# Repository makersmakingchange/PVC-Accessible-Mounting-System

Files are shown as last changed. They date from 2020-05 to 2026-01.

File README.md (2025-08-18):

# PVC Assistive Mounting System

The PVC Assistive Mounting System is a collection of readily available commercial-off-the-shelf components and 3D printed components that can be assembled into various configurations to provide mounting solutions for assistive technology.

## Configurations

### LipSync Desk Mount
The [LipSync Desk Mount](/Configurations/LipSync_Desk_Mount/README.md) provides a low cost, adjustable system to mount the [LipSync Classic](https://github.com/makersmakingchange/LipSync-Classic) to a flat surface like a table or desk.

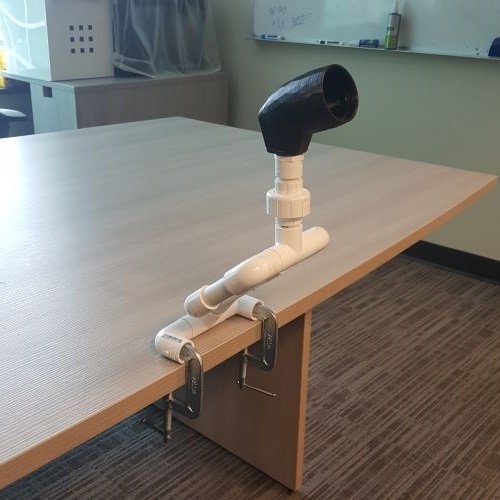
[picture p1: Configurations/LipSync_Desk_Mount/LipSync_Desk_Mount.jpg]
LipSync Desk Mount


### Small Button Mount
The [Small Button Mount](/Configurations/Small_Button_Mount/README.md) is a simple, inexpensive mounting solution to position a small button on a flat surface.

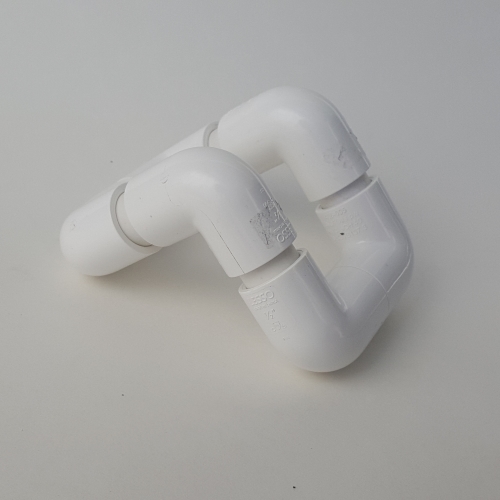
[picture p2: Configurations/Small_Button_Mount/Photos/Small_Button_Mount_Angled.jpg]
Small Button Mount


### Large Button Mount
Work-in-progress

## Components
### Camera Quick Clamp
The [PAMS Camera Quick Clamp](Components/PAMS_Camera_Quick_Clamp/README.md) is a 3D printed adapter for attaching an assistive device to a section of 1/2 inch PVC piping. The clamp has a ¼”- 20 UNC camera thread stud that is compatible with various assistive devices and/or camera mount adapters. The clamp can easily be installed, adjusted, and removed by hand.

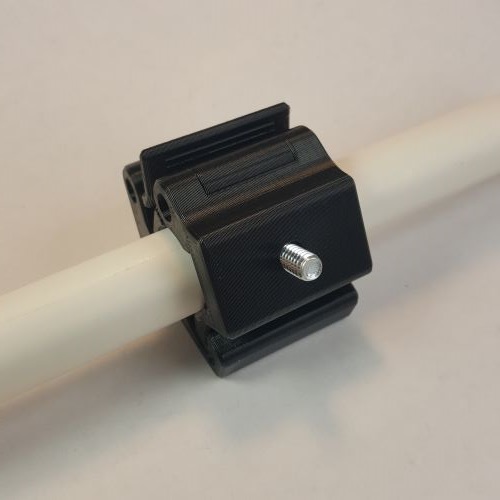
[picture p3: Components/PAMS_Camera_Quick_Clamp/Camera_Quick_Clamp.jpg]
PAMS Camera Quick Clamp


### Super Clamp Adapter
Work-in-progress

### Round Tubing Clamp
Work-in-progress

### Wheelchair Rail adapter
Work-in-progress

## Resources
More information for working with PVC: [PVC Resources](/Resources/README.md)

## License
<br /><span xmlns:dct="http://purl.org/dc/terms/" property="dct:title">PVC Accessible Mounting System</span> by <a xmlns:cc="http://creativecommons.org/ns#" href="www.makersmakingchange.com" property="cc:attributionName" rel="cc:attributionURL">Neil Squire</a> is licensed under a <a rel="license" href="http://creativecommons.org/licenses/by-sa/4.0/">Creative Commons Attribution-ShareAlike 4.0 International License</a>.

<!-- ABOUT MMC START -->
## About Makers Making Change
[Makers Making Change Logo](https://www.makersmakingchange.com/)

Makers Making Change is a program of [Neil Squire](https://www.neilsquire.ca/), a Canadian non-profit that uses technology, knowledge, and passion to empower people with disabilities.

Makers Making Change leverages the capacity of community based Makers, Disability Professionals and Volunteers to develop and deliver affordable Open Source Assistive Technologies.

 - Website: [www.MakersMakingChange.com](https://www.makersmakingchange.com/)
 - GitHub: [makersmakingchange](https://github.com/makersmakingchange)
 - Bluesky: [@makersmakingchange.bsky.social](https://bsky.app/profile/makersmakingchange.bsky.social)
 - Instagram: [@makersmakingchange](https://www.instagram.com/makersmakingchange)
 - Facebook: [makersmakechange](https://www.facebook.com/makersmakechange)
 - LinkedIn: [Neil Squire Society](https://www.linkedin.com/company/neil-squire-society/)
 - Thingiverse: [makersmakingchange](https://www.thingiverse.com/makersmakingchange/about)
 - Printables: [MakersMakingChange](https://www.printables.com/@MakersMakingChange)

### Contact Us
For technical questions, to get involved, or to share your experience we encourage you to [visit our website](https://www.makersmakingchange.com/) or [contact us](https://www.makersmakingchange.com/s/contact).
<!-- ABOUT MMC END -->

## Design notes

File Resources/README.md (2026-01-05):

# PVC Resources

## Suppliers
PVC is readily available at hardware stores.

Home Depot [Canada](https://www.homedepot.ca/)
 - PVC Pipe
 - Standard fittings
 - Tools

Amazon
[Ventral](https://www.amazon.ca/PVC-Pipe-SCH-Inch-White/dp/B00V67XP0)

[McMaster-Carr](https://www.mcmaster.com/)
 - Pipe [5ft](https://www.mcmaster.com/48925K91) [10ft](https://www.mcmaster.com/48925K11)
 - [Fittings](https://www.mcmaster.com/pvc-(schedule-40)-pipe-fittings)

[PVCFittingsOnline](https://www.pvcfittingsonline.com/)
 - Pipe
 - Standard fittings
 - Specialized Fittings
 - Tools

[FORMUFIT](https://formufit.com/)
 - Furniture Grade PVC and SCH 40 PVC in various sizes and colors
 - Specialized Fittings
 - Colored PVC Shrink Covering
 - How-to Guides

 [Lee Valley](https://www.leevalley.com/)
  - [Specialized fittings](https://www.leevalley.com/en-us/shop/garden/planting/greenhouse/67332-pvc-connectors)
     - Slip-T
     - 45 deg Elbow
     - 90 deg Elbow
     - 3-Way - T
     - 4-Way Cross
     - 3-Way Branch
     - 4-Way Branch
     - 5-Way Branch

## Resources

1. Assistive Technology Educational Network (ATEN). (2005). **PVC: Practical, Versatile, Cheap Assistive Technology Supports"**. Copy available in repository [here](https://github.com/makersmakingchange/PVC-Accessible-Mounting-System/blob/main/Resources/PVC-Practical_Versatile_Cheap_Assistive_Technology_Supports.pdf).  
    - Basics of cutting, gluing, and finishing PVC easily and safely
    - Numerous designs:
        - Adapted Writing Aid
        - Stove Knob Turner
        - Toy Corral
        - Small Switch Stand
        - Large Switch Stand
        - DynaVox Stand
        - Sensory Stimulation Stand
        - Felt Story Board
        - Dual-Angle Easel
        - Adjustable Height Switch Mount
        - Toy Bowling Ball Launcher
        - Number Line
        - Communication Stand
        - Tilting Eye Gaze Frame
        - Circle
        - Auditory Feedback Phone
        - Multi-Purpose Easel
        - Protected Object Display
        - Floor Mobile Stand
        - 4 Shelf Locker Organizer
        - Sand/Water Table

2. Aardvark/Collins International. (1982). **Tinker tubes: personal lighting systems**. Free low-resolution copy available at https://www.software-cinema.com/page/13/tinkertubes.

## Other Assistive Technology Projects Using PVC

PVC Therapy Trike
https://www.instructables.com/id/PVC-Therapy-Trike/

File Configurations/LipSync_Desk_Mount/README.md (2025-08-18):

# PAMS - LipSync Desk Mount
The LipSync Desk Mount provides a low cost, adjustable configuration to mount the [LipSync](https://www.makersmakingchange.com/project/lipsync/) to a flat surface like a table or desk. The Lipsync can be attached directly to mount or using different components to provide greater flexibility. The mount attaches to the surface using two c-clamps, which can be purchased in different sizes to accommodate different desk and table thicknesses.   The LipSync Desk Mount is part of the PVC Assistive Mounting System (PAMS).

The [PVC Assistive Mounting System](https://github.com/makersmakingchange/PVC-Accessible-Mounting-System) is a collection of readily available commercial-off-the-shelf components and 3D printed components that can be assembled into various configurations to provide mounting solutions for assistive technology.

PAMS LipSync Desk Mount

## More info at
- [Makers Making Change Project Page](https://www.makersmakingchange.com/project/pams-lipsync-desk-mount/)

## Documentation
| Document             | Version | Link |
|----------------------|---------|------|
| Design Specification | WIP     |  n/a   |
| Design Rationale     | WIP     |  n/a   |
| Bill of Materials    | 0.2     | [LipSync_Desk_Mount_BOM_v0.2](/Configurations/LipSync_Desk_Mount/Documentation/LipSync_Desk_Mount_BOM_v0.2.pdf)    |
| Assembly Guide       | 0.2     | [LipSync_Desk_Mount_Assembly_v0.2](/Configurations/LipSync_Desk_Mount/Documentation/LipSync_Desk_Mount_Assembly_v0.2.pdf)   |
| Maker Checklist      | 0.2     | [LipSync_Desk_Mount_Checklist_v0.2](/Configurations/LipSync_Desk_Mount/Documentation/LipSync_Desk_Mount_Checklist_v0.2.pdf)      |
| User Guide           | 0.2     | [LipSync_Desk_Mount_UserGuide_v0.2](/Configurations/LipSync_Desk_Mount/Documentation/LipSync_Desk_Mount_UserGuide_v0.2.pdf)      |
| Changes              | 0.2     | [LipSync_Desk_Mount_Changelog_v0.2](/Configurations/LipSync_Desk_Mount/Documentation/LipSync_Desk_Mount_Changelog_v0.2.pdf)      |

## Design Files
n/a

## Build Files
n/a

## License

<br /><span xmlns:dct="http://purl.org/dc/terms/" property="dct:title">LipSync Desk Mount</span> by <a xmlns:cc="http://creativecommons.org/ns#" href="www.makersmakingchange.com" property="cc:attributionName" rel="cc:attributionURL">Neil Squire</a> is licensed under a <a rel="license" href="http://creativecommons.org/licenses/by-sa/4.0/">Creative Commons Attribution-ShareAlike 4.0 International License</a>.

<!-- ABOUT MMC START -->
## About Us

Makers Making Change Logo

Makers Making Change is an initiative of [Neil Squire](https://www.neilsquire.ca/), a Canadian non-profit that helps people with disabilities.

We are committed to creating a network of volunteer makers who support people with disabilities in their communities through 3D printing assistive devices. Check out our library of free, open-source assistive technologies with parts and build instructions.

 - [www.MakersMakingChange.com](https://www.makersmakingchange.com/)
 - [GitHub](https://github.com/makersmakingchange)
 - [Thingiverse](https://www.thingiverse.com/makersmakingchange/about)
 - Twitter: [@makermakechange](https://twitter.com/makermakechange)
 - Instagram: [@makersmakingchange](https://www.instagram.com/makersmakingchange)

## Contact Us

For technical questions, to get involved, or share your experience we encourage you to visit the [MMC Project Page](https://www.makersmakingchange.com/project/pams-lipsync-desk-mount/), [MMC Forum](hhttps://forum.makersmakingchange.com/t/pams-lipsync-desk-mount/850), or contact info@makersmakingchange.com
<!-- ABOUT MMC END -->

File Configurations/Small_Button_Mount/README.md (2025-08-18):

# PAMS - Small Button Mount
The Small Button Mount is a simple, inexpensive mounting solution to position small buttons on a flat surface. The Small Button Mount is a part of the PVC Assistive Mounting System (PAMS).

The [PVC Assistive Mounting System](https://github.com/makersmakingchange/PVC-Accessible-Mounting-System) is a collection of readily available commercial-off-the-shelf components and 3D printed components that can be assembled into various configurations to provide mounting solutions for assistive technology.

Small Button Mount

## More info at
- [Makers Making Change Project Page](https://www.makersmakingchange.com/project/pams-small-button-mount/)

## Documentation
| Document             | Version | Link |
|----------------------|---------|------|
| Design Specification | WIP     |  n/a   |
| Design Rationale     | WIP     |  n/a   |
| Bill of Materials    | 0.1     | [Small_Button_Mount_BOM_v0.1](/Configurations/Small_Button_Mount/Documentation/Small_Button_Mount_BOM_v0.1.pdf)    |
| Assembly Guide       | 0.1     | [Small_Button_Mount_Assembly_v0.1](/Configurations/Small_Button_Mount/Documentation/Small_Button_Mount_Assembly_v0.1.pdf)   |
| Maker Checklist      | 0.1     | [Small_Button_Mount_Checklist_v0.1](/Configurations/Small_Button_Mount/Documentation/Small_Button_Mount_Checklist_v0.1.pdf)      |
| User Guide           | 0.1     | [Small_Button_Mount_UserGuide_v0.1](/Configurations/Small_Button_Mount/Documentation/Small_Button_Mount_UserGuide_v0.1.pdf)      |
| Changes              | 0.1     | [Small_Button_Mount_Changelog_v0.1](/Configurations/Small_Button_Mount/Documentation/Small_Button_Mount_Changelog_v0.1.pdf)      |

## Design Files
n/a

## Build Files
n/a

## License
<br /><span xmlns:dct="http://purl.org/dc/terms/" property="dct:title">Small Button Mount</span> by <a xmlns:cc="http://creativecommons.org/ns#" href="www.makersmakingchange.com" property="cc:attributionName" rel="cc:attributionURL">Neil Squire</a> is licensed under a <a rel="license" href="http://creativecommons.org/licenses/by-sa/4.0/">Creative Commons Attribution-ShareAlike 4.0 International License</a>.

<!-- ABOUT MMC START -->
## About Us
Makers Making Change Logo

Makers Making Change is an initiative of [Neil Squire](https://www.neilsquire.ca/), a Canadian non-profit that helps people with disabilities.

We are committed to creating a network of volunteer makers who support people with disabilities in their communities through 3D printing assistive devices. Check out our library of free, open-source assistive technologies with parts and build instructions.

 - [www.MakersMakingChange.com](https://www.makersmakingchange.com/)
 - [GitHub](https://github.com/makersmakingchange)
 - [Thingiverse](https://www.thingiverse.com/makersmakingchange/about)
 - Twitter: [@makermakechange](https://twitter.com/makermakechange)
 - Instagram: [@makersmakingchange](https://www.instagram.com/makersmakingchange)

## Contact Us
For technical questions, to get involved, or share your experience we encourage you to visit the [MMC Project Page](https://www.makersmakingchange.com/project/pams-small-button-mount/), [MMC Forum](https://forum.makersmakingchange.com/t/pams-small-button-mount/851), or contact info@makersmakingchange.com
<!-- ABOUT MMC END -->

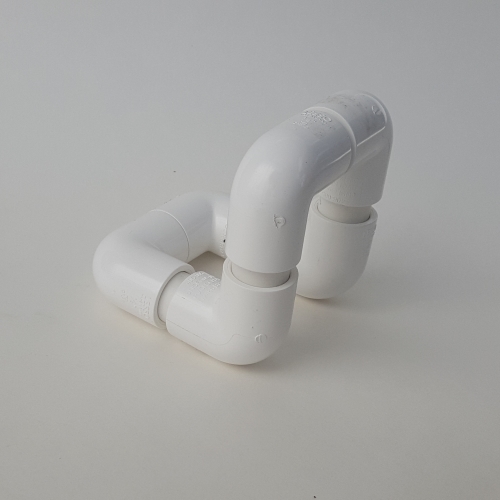
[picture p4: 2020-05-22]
Configurations/Small_Button_Mount/Photos/Small_Button_Mount_Upright.jpg

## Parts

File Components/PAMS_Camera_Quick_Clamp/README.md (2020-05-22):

# PAMS - Camera Quick Clamp
The Camera Quick Clamp is an 3D printed adapter for attaching an assistive device to a section of 1/2 inch PVC piping. The clamp has a ¼”- 20 UNC camera thread stud that is compatible with various assistive devices and/or camera mount adapters. The clamp can easily be installed, adjusted, and removed by hand. The Camera Quick Clamp is part of the PVC Assistive Mounting System (PAMS).

The [PVC Assistive Mounting System](https://github.com/makersmakingchange/PVC-Accessible-Mounting-System) is a collection of readily available commercial-off-the-shelf components and 3D printed components that can be assembled into various configurations to provide mounting solutions for assistive technology.

PAMS Camera Quick Clamp

## More info at
- [Makers Making Change Project Page](https://www.makersmakingchange.com/project/pams-camera-quick-clamp/)
- [Makers Making Change Forum Thread](https://forum.makersmakingchange.com/t/pams-camera-quick-clamp/728)

## Documentation
| Document             | Version | Link |
|----------------------|---------|------|
| Design Specification | WIP     |      |
| Design Rationale     | WIP     |      |
| Bill of Materials    | WIP     |      |
| Assembly Guide       | 0.1     | [Camera_Quick Clamp_Assembly_v0.1](/Components/PAMS_Camera_Quick_Clamp/Documentation/Camera_Quick_Guide_v0.1.pdf)     |
| Maker Checklist      | 0.1     | [Camera_Quick_Clamp_Checklist_v0.1](/Components/PAMS_Camera_Quick_Clamp/Documentation/Camera_Quick_Clamp_Checklist_v0.1.pdf)     |
| User Guide           | 0.1     |  [Camera_Quick_Clamp_UserGuide_v0.1](/Components/PAMS_Camera_Quick_Clamp/Documentation/Camera_Quick_Clamp_UserGuide_v0.1.pdf)    |
| Changelog              | WIP     |      |

## Design Files
[CAD Files](/Components/PAMS_Camera_Quick_Clamp/CAD_Files)

## Build Files
[3D Printing Files](/Components/PAMS_Camera_Quick_Clamp/3D_Print_Files)

## Attribution
The snap latch mechanism was inspired by [NASA CHAMP CLAMP (Strong man)](https://grabcad.com/library/nasa-champ-clamp-strong-man-1) by [Jonathan Brazeau](https://grabcad.com/jonathan.brazeau-3).

## License
<br /><span xmlns:dct="http://purl.org/dc/terms/" property="dct:title">PAMS Camera Quick Clamp</span> by <a xmlns:cc="http://creativecommons.org/ns#" href="www.makersmakingchange.com" property="cc:attributionName" rel="cc:attributionURL">Neil Squire</a> is licensed under a <a rel="license" href="http://creativecommons.org/licenses/by-sa/4.0/">Creative Commons Attribution-ShareAlike 4.0 International License</a>.

## About Us

Makers Making Change Logo

Makers Making Change is an initiative of [Neil Squire](https://www.neilsquire.ca/), a Canadian non-profit that helps people with disabilities.

We are committed to creating a network of volunteer makers who support people with disabilities in their communities through 3D printing assistive devices. Check out our library of free, open-source assistive technologies with parts and build instructions.

 - [www.MakersMakingChange.com](https://www.makersmakingchange.com/)
 - [GitHub](https://github.com/makersmakingchange)
 - [Thingiverse](https://www.thingiverse.com/makersmakingchange/about)
 - Twitter: [@makermakechange](https://twitter.com/makermakechange)
 - Instagram: [@makersmakingchange](https://www.instagram.com/makersmakingchange)

## Contact Us

For technical questions, to get involved, or share your experience we encourage you to visit the [MMC Project Page]( https://www.makersmakingchange.com/project/pams-camera-quick-clamp/), [MMC Forum](https://forum.makersmakingchange.com/t/pams-camera-quick-clamp/728), or contact info@makersmakingchange.com

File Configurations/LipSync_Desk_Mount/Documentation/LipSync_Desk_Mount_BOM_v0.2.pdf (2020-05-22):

# Lipsync PVC Mounting Kit: BOM

## COTS Parts

PBS # | Name | Source | Part Number | Qty | Cost Per | Total Cost | Unit Qty | Unit Cost | Min Order | Min Order Cost | Notes Link
Union | Home Depot | 1 | 3.74 | 3.74 1 3.74 1 3.74 1 foot length https://www.homedepot.ca/product/lesso-pvc-union-with-o-ring-seal-soc-x-soc-1-2-inch/1000111070
Straight Adapter, Female Soc x Female Threaded | Home Depot | 0 | 0.89 | 0.00 1 0.89 0 0.00 1 foot length https://www.homedepot.ca/product/carlon-schedule-40-pvc-female-adapter-1-2-inch/1000100870
Straight Adapter, Female Soc x Male Threaded | Home Depot | 1 | 0.89 | 0.89 1 0.89 1 0.89 | https://www.homedepot.ca/product/thomas-betts-schedule-40-pvc-male-terminal-adapter-1-2-inch/1000100884
Tee | Home Depot | 3 | 0.66 | 1.98 1 0.66 3 1.98 | https://www.homedepot.ca/product/lesso-pvc-tee-soc-x-soc-x-soc-1-2-inch/1000166805
Tee S x S x FIPT | Home Depot | 0 | 0.48 | 0.00 1 0.48 0 0.00 | https://www.homedepot.ca/product/nibco-1-2-in-pvc-schedule-40-tee-s-x-s-x-fipt/1000166798
Elbow | Home Depot | 6 | 1.12 | 6.72 1 1.12 6 6.72 | https://www.homedepot.ca/product/nibco-1-2-in-pvc-schedule-40-90-degree-elbow/1000166792
PVC Piping | Home Depot | 0.1 | 0.95 | 0.09 10 9.48 1 9.48
C-Clamp 2 in | Home Depot | 2 | 5.55 | 11.10 1 5.55 2 11.10
| | | | 24.52 33.91

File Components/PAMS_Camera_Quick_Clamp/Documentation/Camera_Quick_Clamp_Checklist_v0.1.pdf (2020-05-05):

V0.1 | MAY 2020

# PAMS: Camera Quick Clamp

MAKER CHECKLIST

© 2020 by Neil Squire. (https://neilsquire.ca/) “Maker Checklist” is licensed under the CC BY SA 4.0 License: http://creativecommons.org/licenses/by-sa/4.0
Design files available at https://www.makersmakingchange.com/project/pams-camera-quick-clamp/ (https://www.makersmakingchange.com/?post_type=project&p=4509&preview=true) | PAGE 1 OF 1

To-do

ð Acquire the off-the-shelf components ð 3D print the 3D printed components ð Assemble the Quick Clamp
ð Clean and disinfect the Quick Clamp ð Package the Quick Clamp in a sealed bag
ð Print the User Guide

Items to Deliver to User

ð Assembled Quick Clamp
ð User Guide

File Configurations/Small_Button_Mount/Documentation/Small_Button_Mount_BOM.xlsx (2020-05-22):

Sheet: Sheet1
PAMS Small Buttom Mount: BOM
COTS Parts
PBS # | Name | Source | Part Number | Qty | Cost Per | Total Cost | Unit Qty | Unit Cost | Min Order | Min Order Cost | Notes | Link
 | Elbow | Home Depot |  | 6 | 1.12 | 6.72 | 1 | 1.12 | 6 | 6.72 |  | https://www.homedepot.ca/product/nibco-1-2-in-pvc-schedule-40-90-degree-elbow/1000166792
 | PVC Piping | Home Depot |  | 0.1 | 0.95 | 0.09 | 10 | 9.48 | 1 | 9.48 | Qty is feet
 |  |  |  |  |  | $6.81 |  |  |  | $16.20

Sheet: Sheet2
Aluminum Rod
https://www.hillmangroup.com/us/en/Home-Solutions/Rods%2C-Shapes%2C-%26-Sheets/Shape/Round---Tube/SteelWorks-Aluminum-Round-Tubes/p/11395
https://www.lowes.ca/product/round-metal-tubes/hillman-3-ft-x-12-in-aluminum-plain-tube-215889

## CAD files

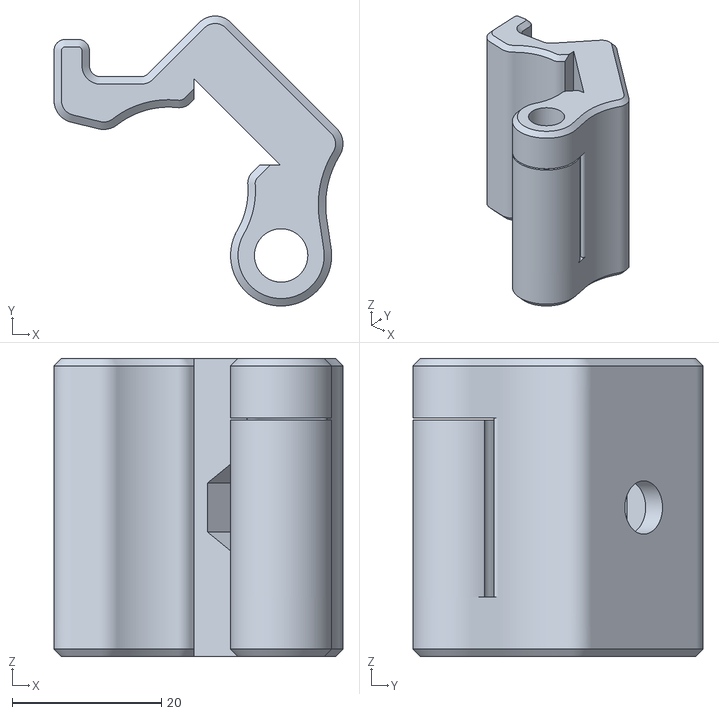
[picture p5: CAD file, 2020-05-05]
Components/PAMS_Camera_Quick_Clamp/3D_Print_Files/CQC_MainBody.stl
38.7 x 38.9 x 40.0

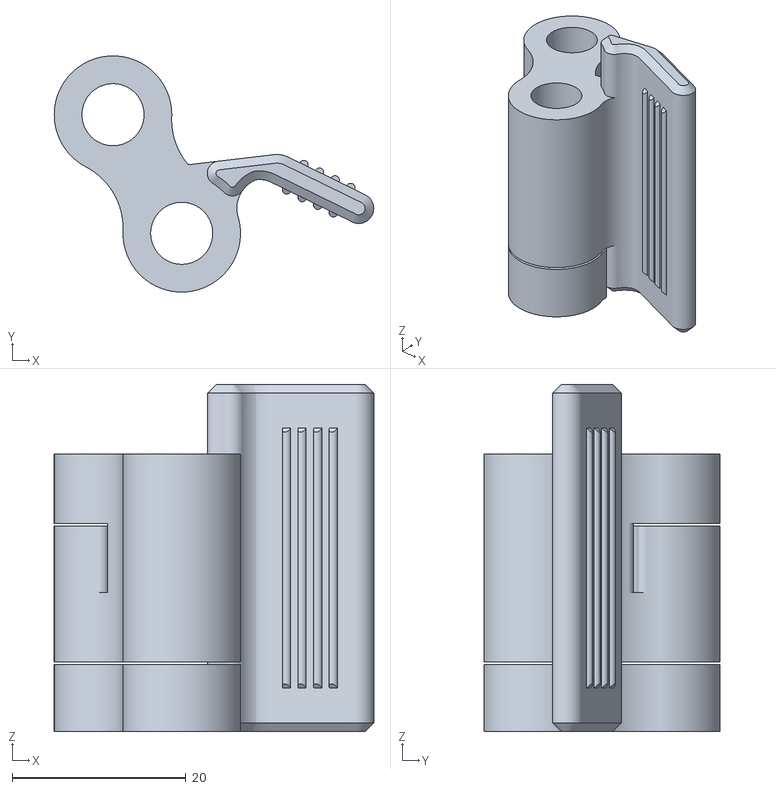
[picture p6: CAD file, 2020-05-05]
Components/PAMS_Camera_Quick_Clamp/3D_Print_Files/CQC_LeverHandle.stl
36.8 x 27.2 x 40.0

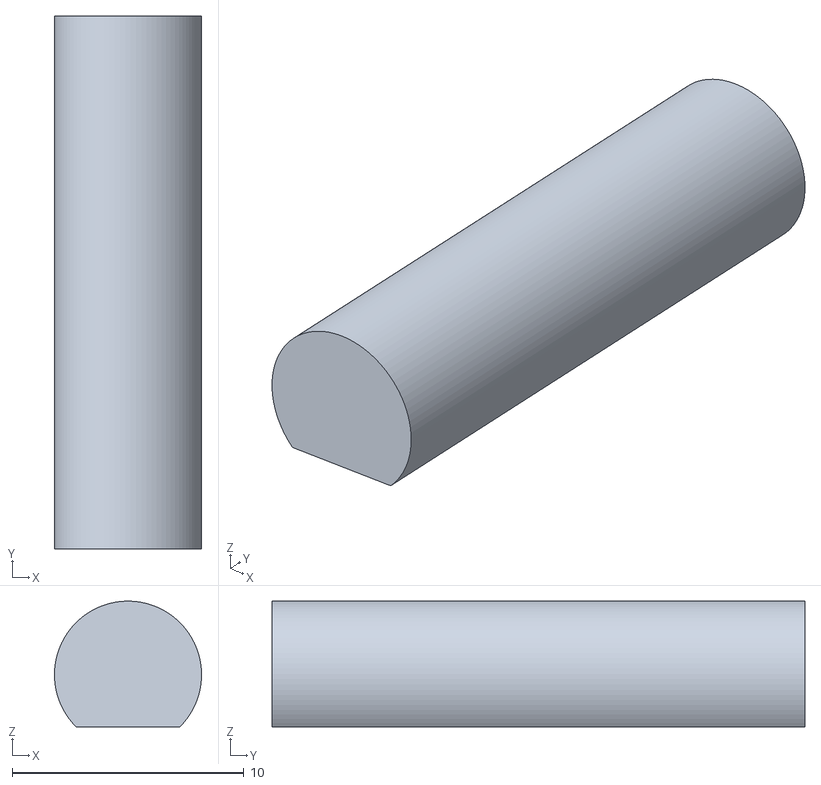
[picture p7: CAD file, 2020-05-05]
Components/PAMS_Camera_Quick_Clamp/3D_Print_Files/CQC_ShortPin.stl
6.35 x 23.0 x 5.42

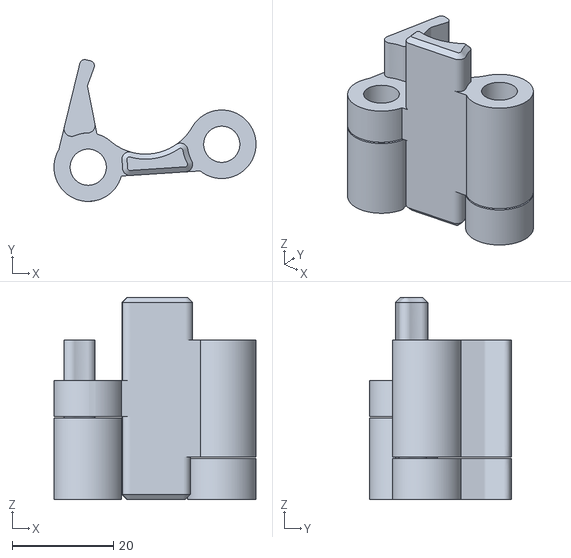
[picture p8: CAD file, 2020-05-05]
Components/PAMS_Camera_Quick_Clamp/3D_Print_Files/CQC_SecondaryBody.stl
40.0 x 28.1 x 40.0

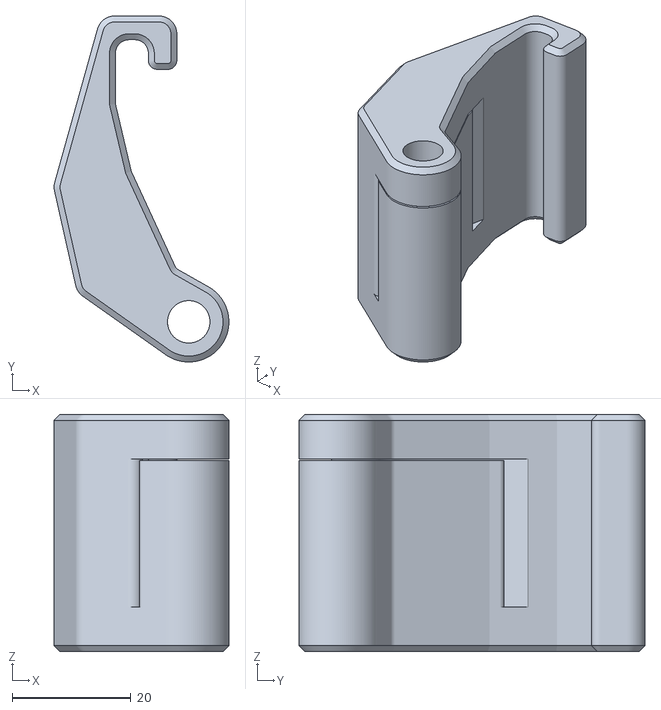
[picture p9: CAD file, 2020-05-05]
Components/PAMS_Camera_Quick_Clamp/3D_Print_Files/CQC_LatchArm.stl
29.5 x 58.3 x 40.0

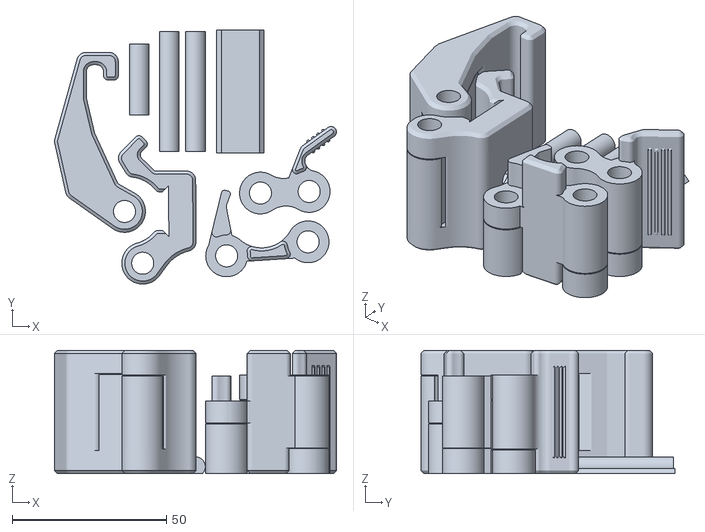
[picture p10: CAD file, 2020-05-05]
Components/PAMS_Camera_Quick_Clamp/3D_Print_Files/CQC.stl
91.4 x 82.4 x 40.0

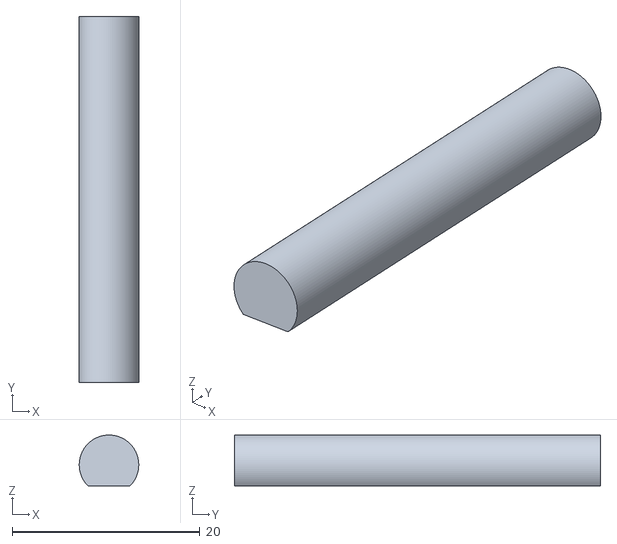
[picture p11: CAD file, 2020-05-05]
Components/PAMS_Camera_Quick_Clamp/3D_Print_Files/CQC_LongPin.stl
6.35 x 39.0 x 5.42

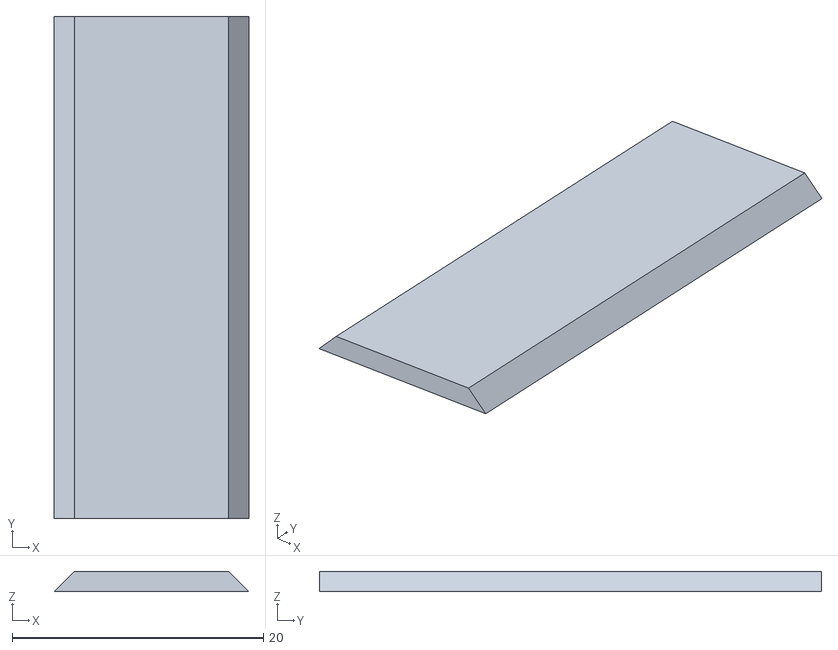
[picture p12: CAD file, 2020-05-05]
Components/PAMS_Camera_Quick_Clamp/3D_Print_Files/CQC_BoltCover.stl
15.5 x 40.0 x 1.60

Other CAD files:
Components/PAMS_Camera_Quick_Clamp/CAD_Files/CQC_v1.0.f3z

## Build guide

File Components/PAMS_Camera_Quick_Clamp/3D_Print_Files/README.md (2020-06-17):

# 3D Print Files
| Component              | Resolution | Infill | Support | Perimeters | Qty |
|-------------------|------------|--------|---------|------------|-----|
| CQC_MainBody      | 0.2 mm     | 20%    | No      | 4          | 1   |
| CQC_SecondaryBody | 0.2 mm     | 20%    | No      | 4          | 1   |
| CQC_LatchArm      | 0.2 mm     | 20%    | No      | 4          | 1   |
| CQC_LeverHandle   | 0.2 mm     | 20%    | No      | 4          | 1   |
| CQC_BoltCover     | 0.2 mm     | 20%    | No      | 4          | 1   |
| CQC_LongPin       | 0.2 mm     | 20%    | No      | 4          | 2   |
| CQC_ShortPin      | 0.2 mm     | 20%    | No      | 4          | 1   |

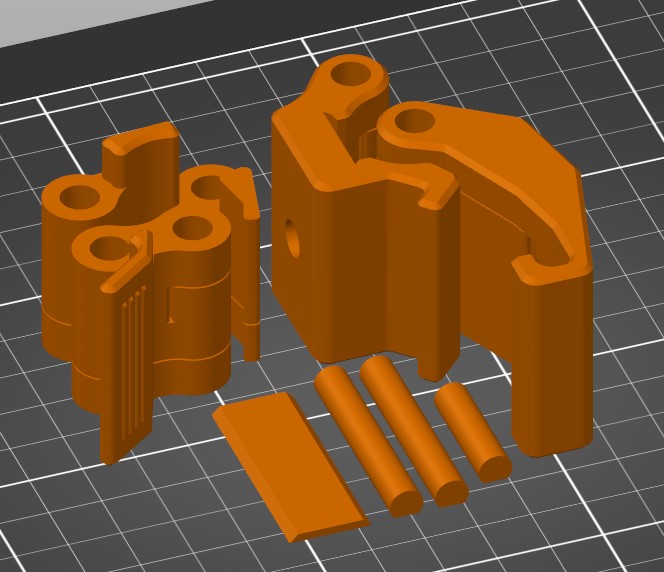
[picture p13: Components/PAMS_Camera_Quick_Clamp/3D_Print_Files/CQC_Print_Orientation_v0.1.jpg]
Screenshot of print orientation


This design uses built-in supports. They will need to be removed before assembly.

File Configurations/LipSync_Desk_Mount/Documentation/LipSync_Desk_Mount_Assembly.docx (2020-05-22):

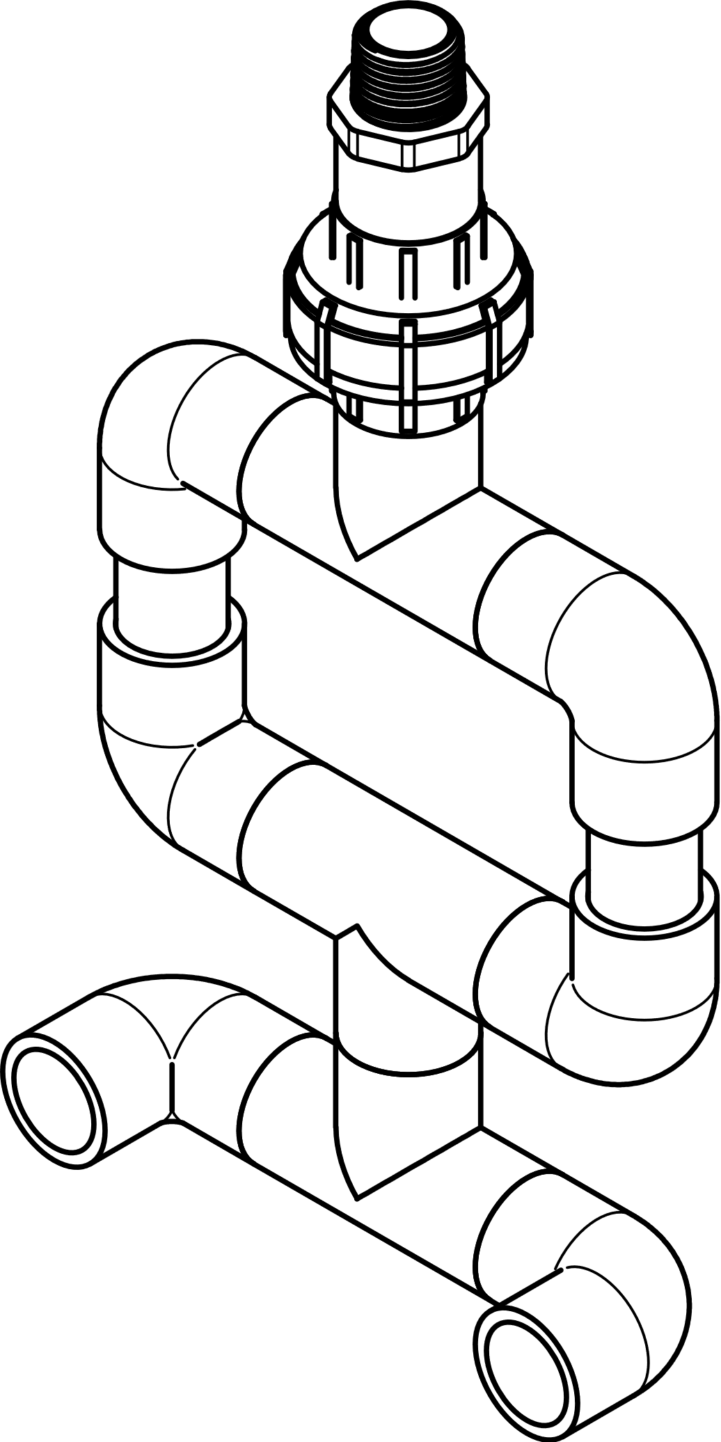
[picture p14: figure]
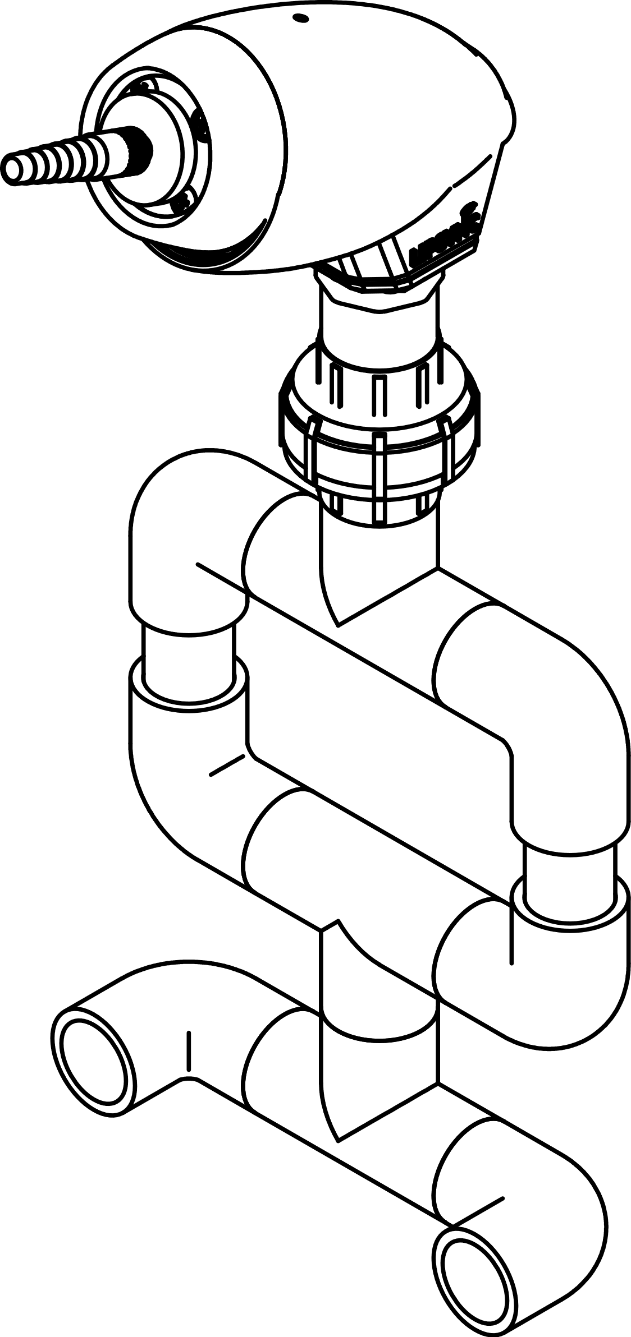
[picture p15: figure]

PARTS

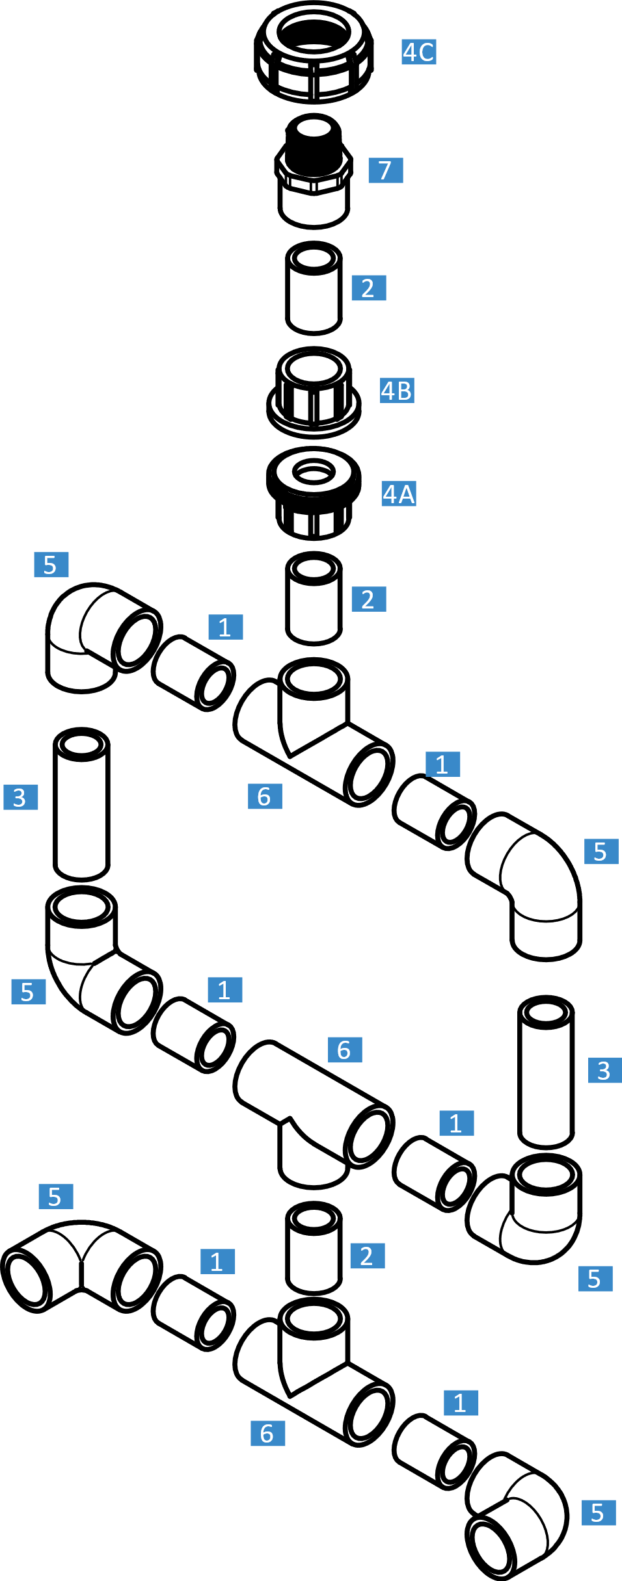
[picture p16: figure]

ID | Description | QTY
1 | PVC Pipe, ½”, 25 mm length | 7
2 | PVC Pipe, ½”, 30 mm length | 3
3 | PVC Pipe, ½”, 60 mm - xx mm length | 2
4 | PVC Union, ½” Soc x ½” Soc | 1
5 | PVC Elbow, ½” Soc x ½” Soc | 6
6 | PVC Tee, ½” Soc x ½” Soc x ½” Soc | 3
7 | PVC Adapter, ½” NPT x ½” Female Soc Adapter | 1
8 | C-Clamp, 2-1/2” | 2

TOOLS AND SUPPLIES

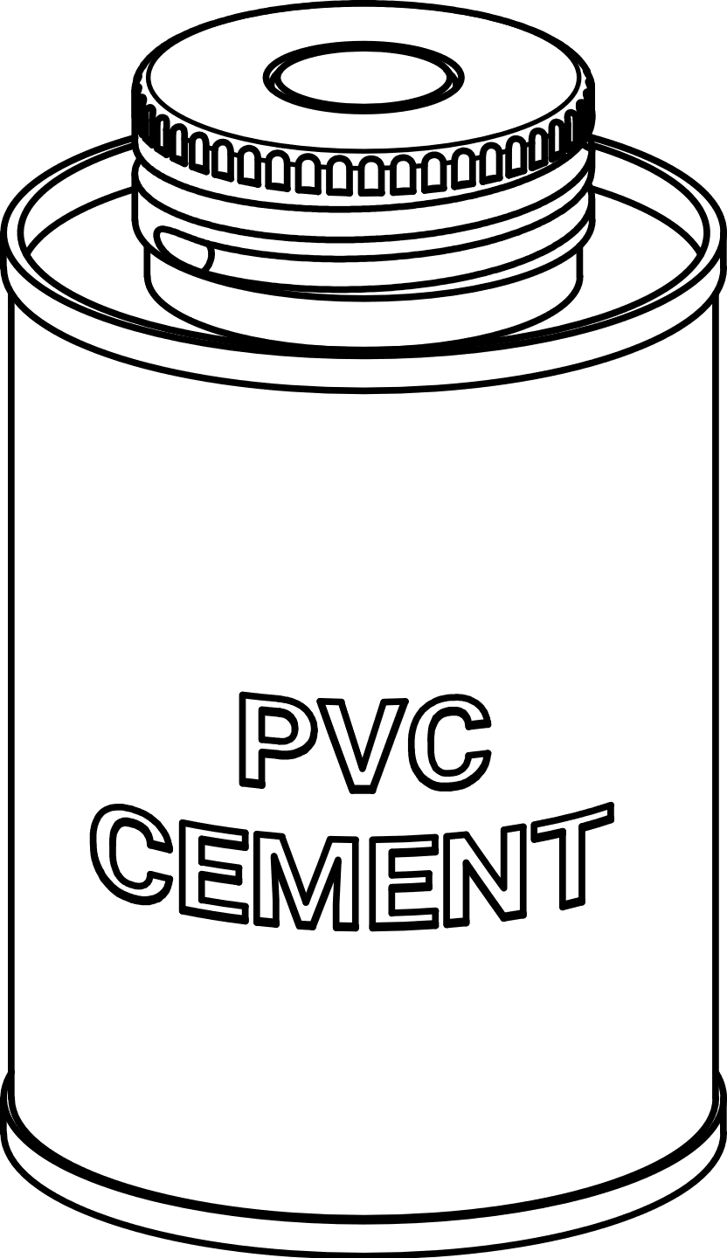
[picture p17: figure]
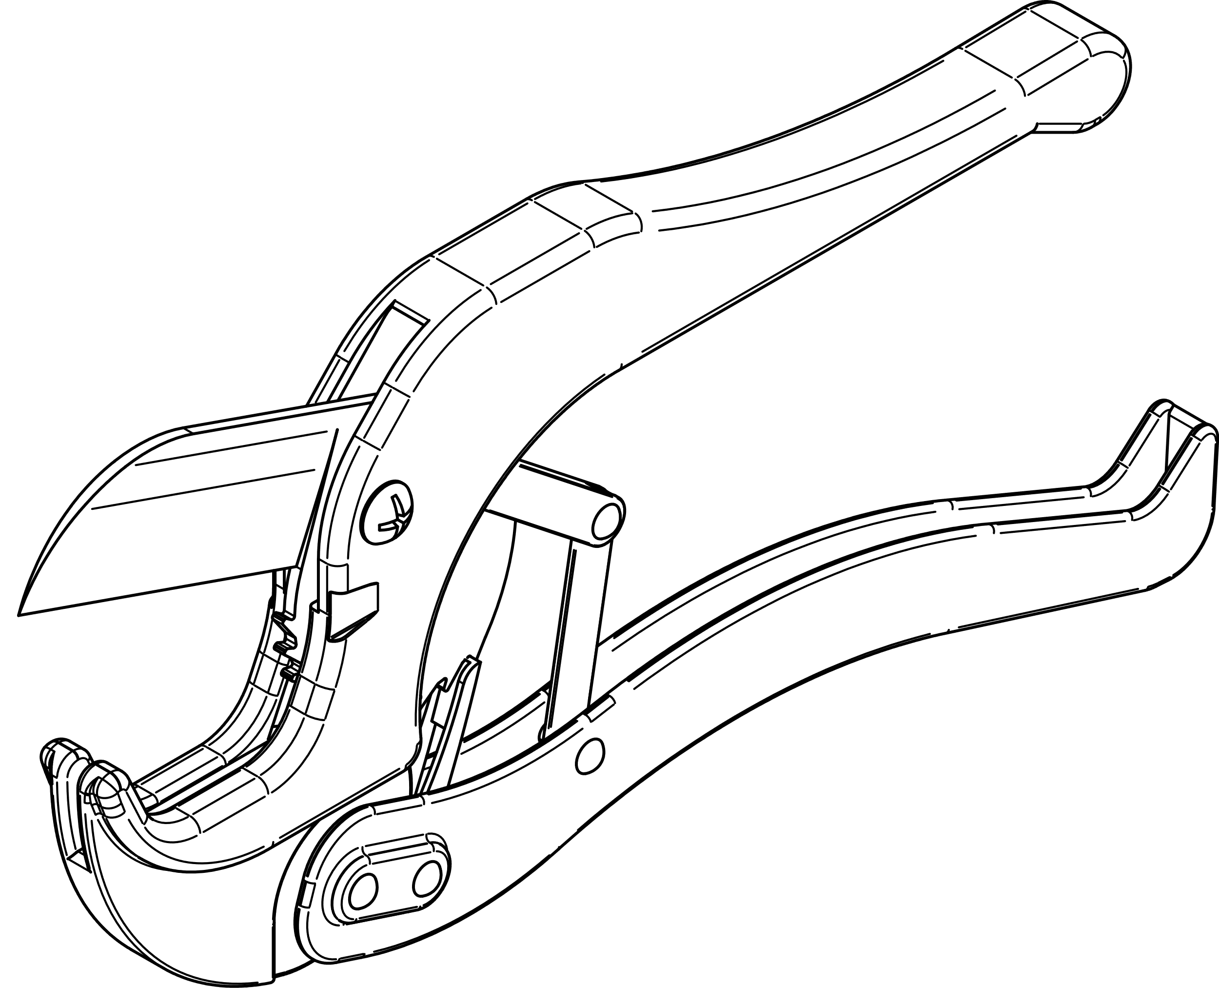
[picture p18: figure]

Description

PVC Cutters OR Hacksaw

PVC Cement (Optional)

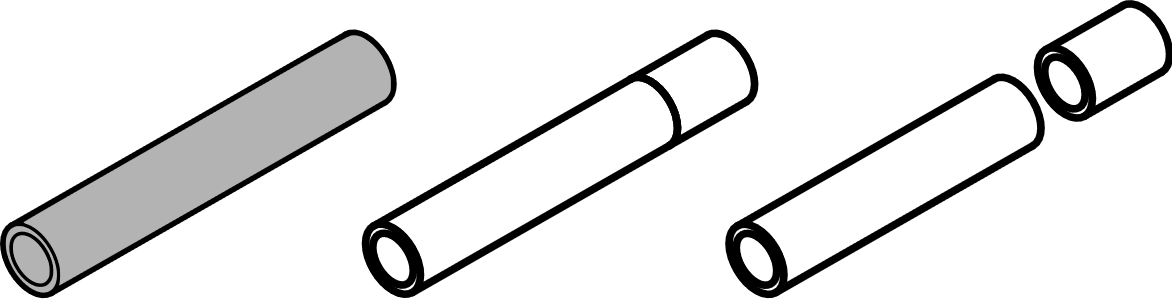
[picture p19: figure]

01. | Use the PVC cutters or hacksaw to cut the PVC pipe to length. | 02. | Insert two short PVC sections into an elbow.
03. | Insert an elbow onto each pipe section. | 04. | Repeat Steps 2 and 3 to create a second side.
05. | Insert longer PVC section into elbows. | 06. | Connect second side.
07. | (Optional) Use pencil to mark lines across joints. | 08. | (Optional) Disassemble and reassemble with PVC cement. Erase pencil marks.

© 2020 by Neil Squire. “Assembly Guide” licensed under the CC BY SA 4.0 License: http://creativecommons.org/licenses/by-sa/4.0 PAGE 1 OF 3 Design files available at https://www.makersmakingchange.com/project/pams-small-button-mount/

V0.2 | MAY 2020 PAMS: LipSync Desk Mount Assembly GUIDE

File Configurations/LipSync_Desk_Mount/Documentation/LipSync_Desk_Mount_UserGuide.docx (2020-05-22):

Introduction

The LipSync Desk Mount is a simple mounting solution for mounting the LipSync to a desk or table using a set of PVC piping components and C-clamps.

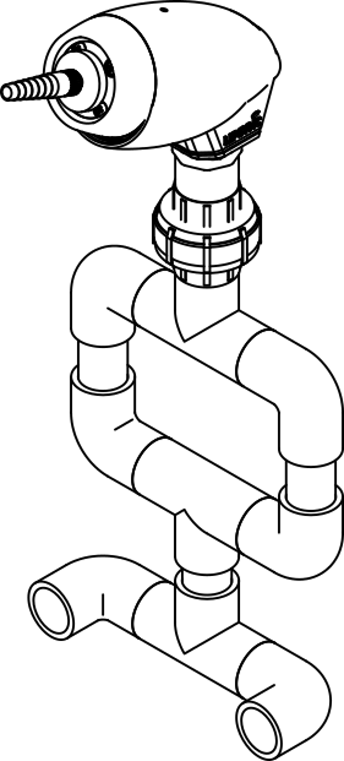
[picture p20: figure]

Features

LipSync

Thread Adapter

Union

Bottom Elbow

Specifications

Size | W 155 mm x D ~50 mm x H ~300 mm
Cleaning | Wipe with damp cloth
Disinfection | Ethyl Alcohol, Isopropyl Alcohol, Hydrogen Peroxide

Attaching the LipSync

1. If present, remove the metal threaded adapter and threaded insert by unscrewing them from the bottom of the LipSync.
2. Being careful not to damage the USB cable, thread the PVC Thread Adapter directly into the 3D printed shell of the LipSync. Do not overtighten.

Mounting to Desk

1. Remove the LipSync from the mount by unscrewing the PVC Union.
2. Use the 2 C-clamps to clamp the bottom PVC Elbows to the table.
3. Reattach the LipSync to the mount by connecting the Union.

Adjusting the Position

The position of the LipSync can be adjusted by manipulating the PVC joints, which are held by friction.

© 2020 by Neil Squire. “User Guide” licensed under the CC BY SA 4.0 License: http://creativecommons.org/licenses/by-sa/4.0 PAGE 1 OF 3 Design files available at https://www.makersmakingchange.com/project/pams-small-button-mount/

V0.2 | MAY 2020 PAMS: LipSync Desk Mount USER GUIDE

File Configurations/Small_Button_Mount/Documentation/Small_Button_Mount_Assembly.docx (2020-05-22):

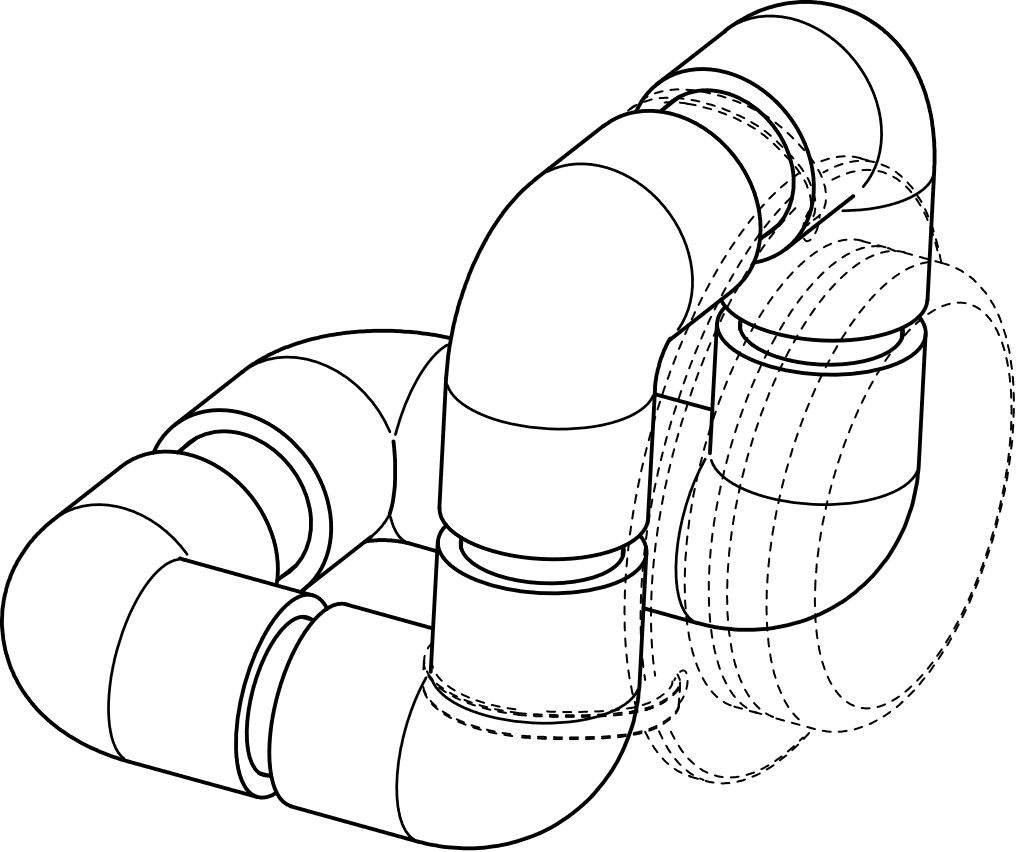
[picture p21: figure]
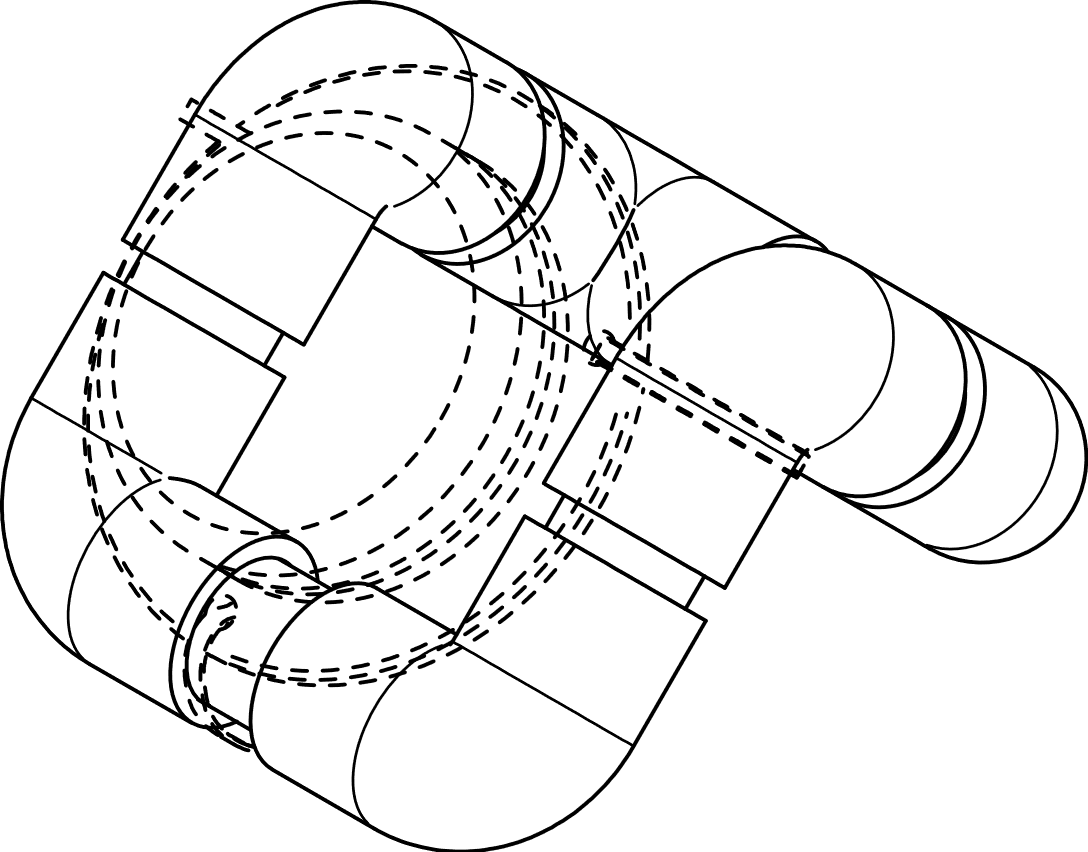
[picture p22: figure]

PARTS

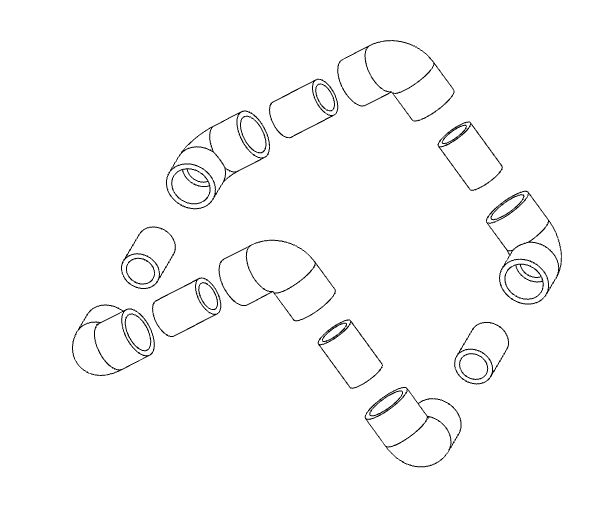
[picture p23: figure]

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
ID | Description | QTY
1 | PVC Elbow 90 deg, ½” | 6
2 | PVC Pipe, ½”, 30 mm length | 4
3 | PVC Pipe, ½”, 30 mm OR 70 mm for use with Quick Clamp | 2

TOOLS AND SUPPLIES


Description

PVC Cutters OR Hacksaw

PVC Cement (Optional)

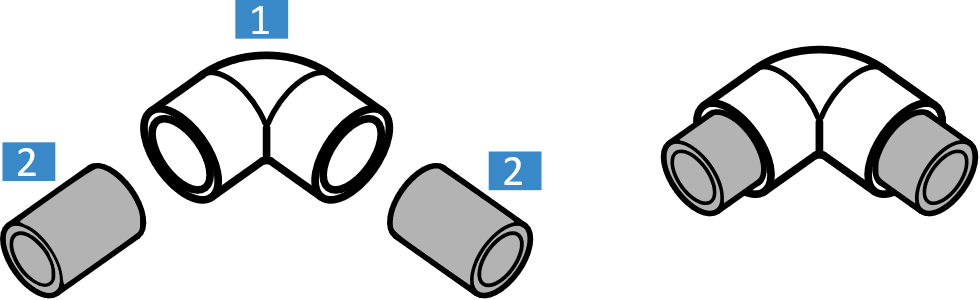
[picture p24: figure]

01. | Use the PVC cutters or hacksaw to cut the PVC pipe to length. | 02. | Insert two short PVC sections into an elbow.

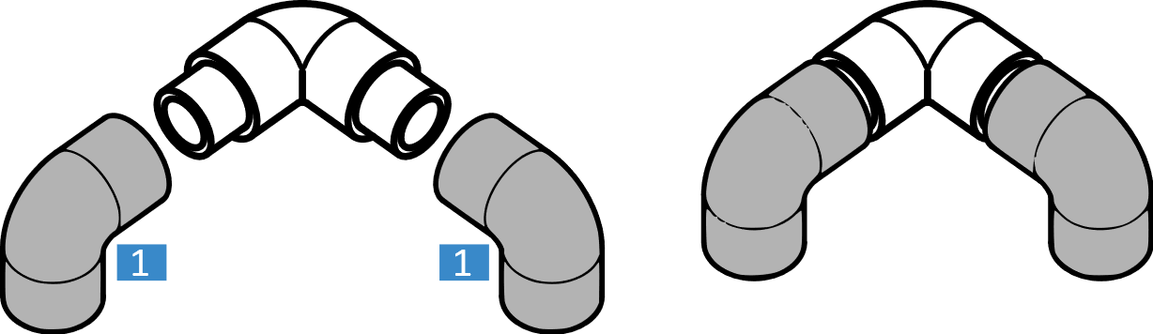
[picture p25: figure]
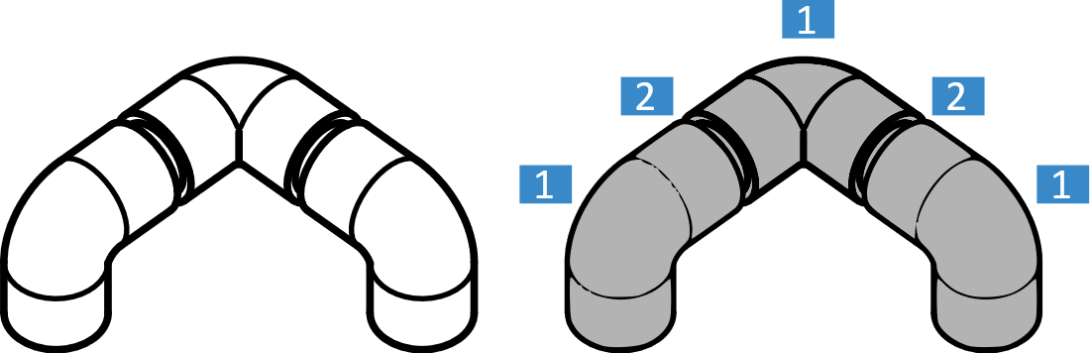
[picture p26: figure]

03. | Insert an elbow onto each pipe section. | 04. | Repeat Steps 2 and 3 to create a second side.

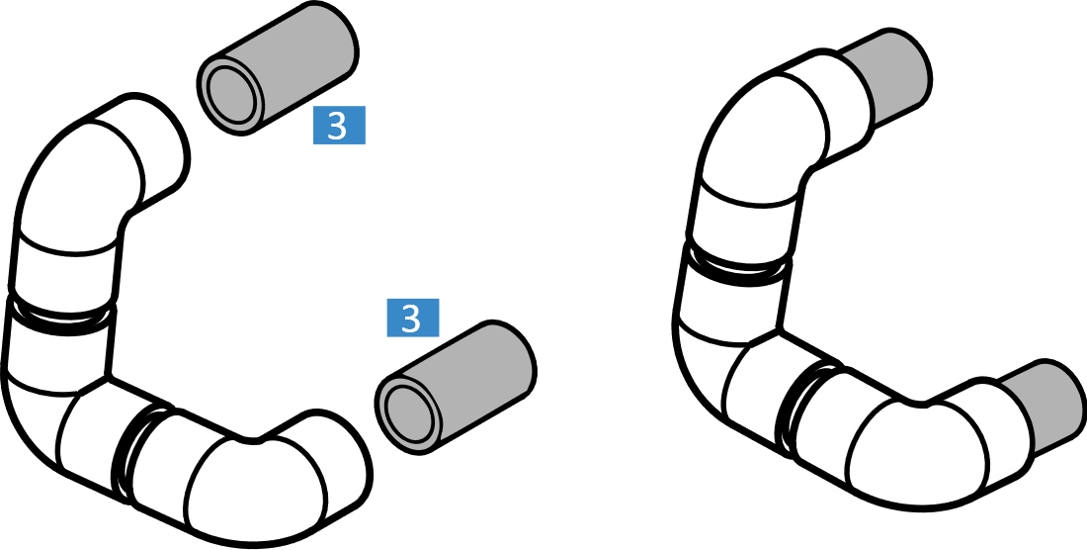
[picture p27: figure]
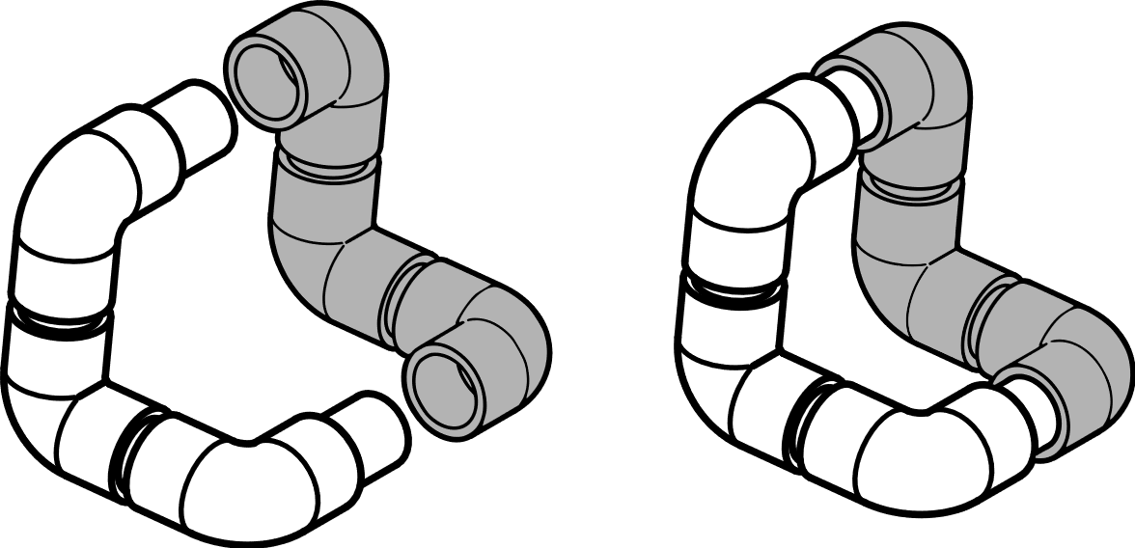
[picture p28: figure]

05. | Insert longer PVC section into elbows. | 06. | Connect second side.

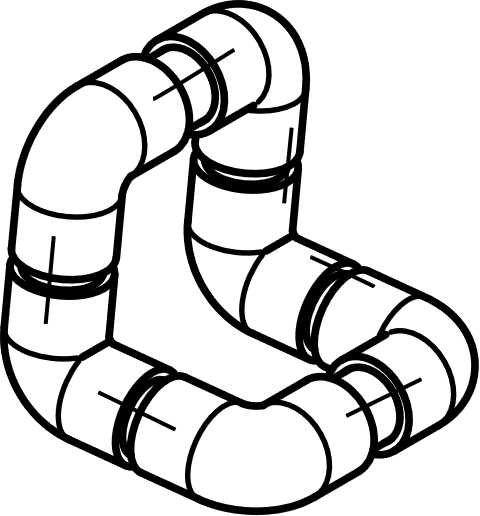
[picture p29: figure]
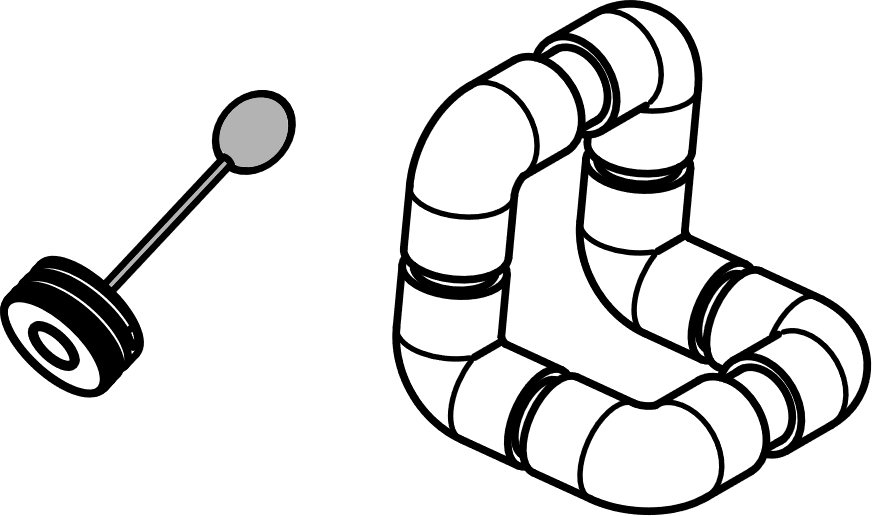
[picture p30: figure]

07. | (Optional) Use pencil to mark lines across joints. | 08. | (Optional) Disassemble and reassemble with PVC cement. Erase pencil marks.

© 2020 by Neil Squire. “Assembly Guide” licensed under the CC BY SA 4.0 License: http://creativecommons.org/licenses/by-sa/4.0 PAGE 1 OF 3 Design files available at https://www.makersmakingchange.com/project/pams-small-button-mount/

V0.1 | MAY 2020 PAMS: Small Button Mount Assembly GUIDE

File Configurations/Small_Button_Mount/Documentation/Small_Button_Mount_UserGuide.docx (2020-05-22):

Introduction

The Small Button Mount is a solution for positioning small switches on a flat surface like a desk or table. It can be used to position a switch at an angle or perpendicular to the surface.


Features

Small Switch

Small Button Mount


Specifications

Size | L 96 mm x W 106 mm x H 96 mm
Disinfection | Ethyl Alcohol, Isopropyl Alcohol, Hydrogen Peroxide

Attaching Switch – Cable Tie

1. Attach button to mount using 3 cable ties (at least 150 mm).

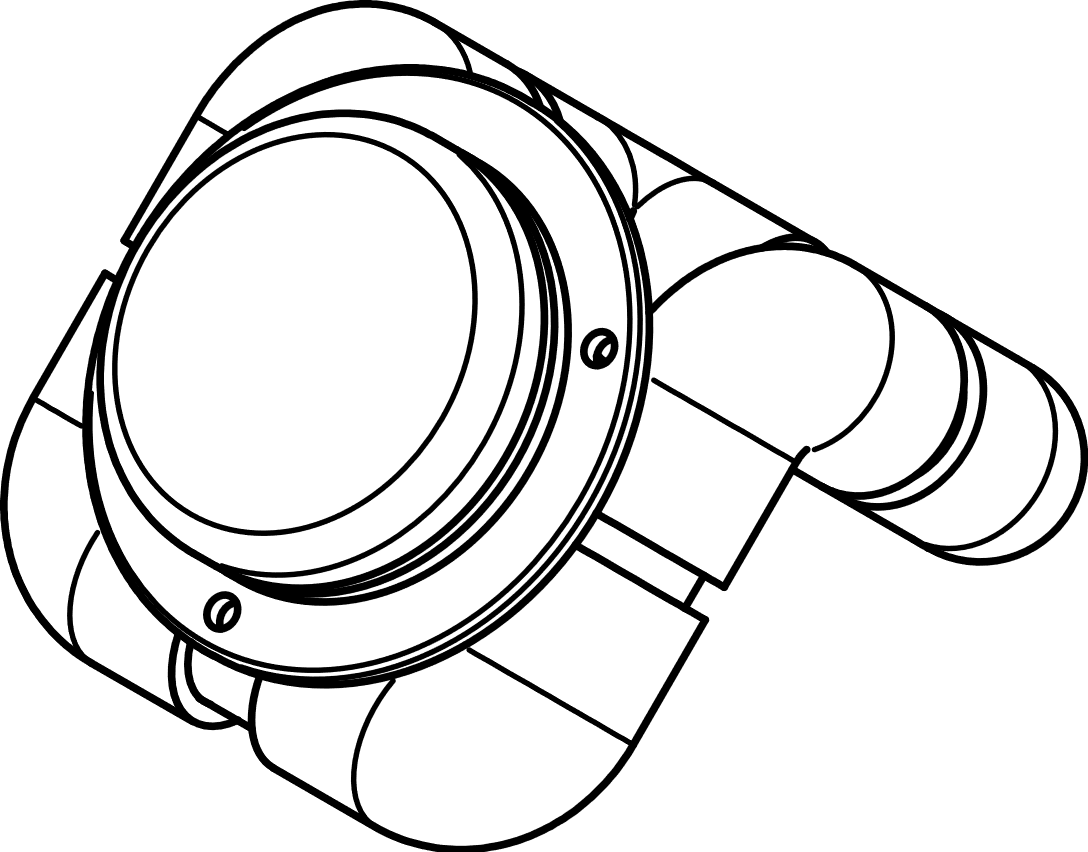
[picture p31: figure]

2. Position the mounted switch.

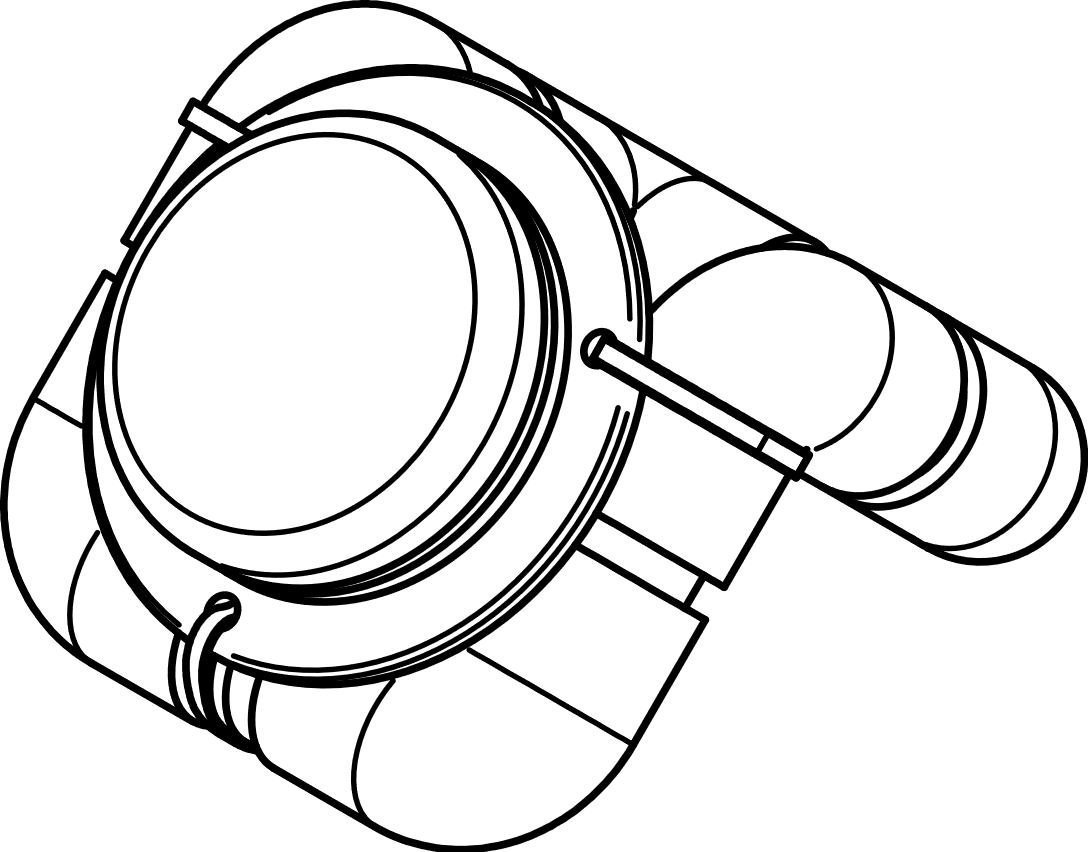
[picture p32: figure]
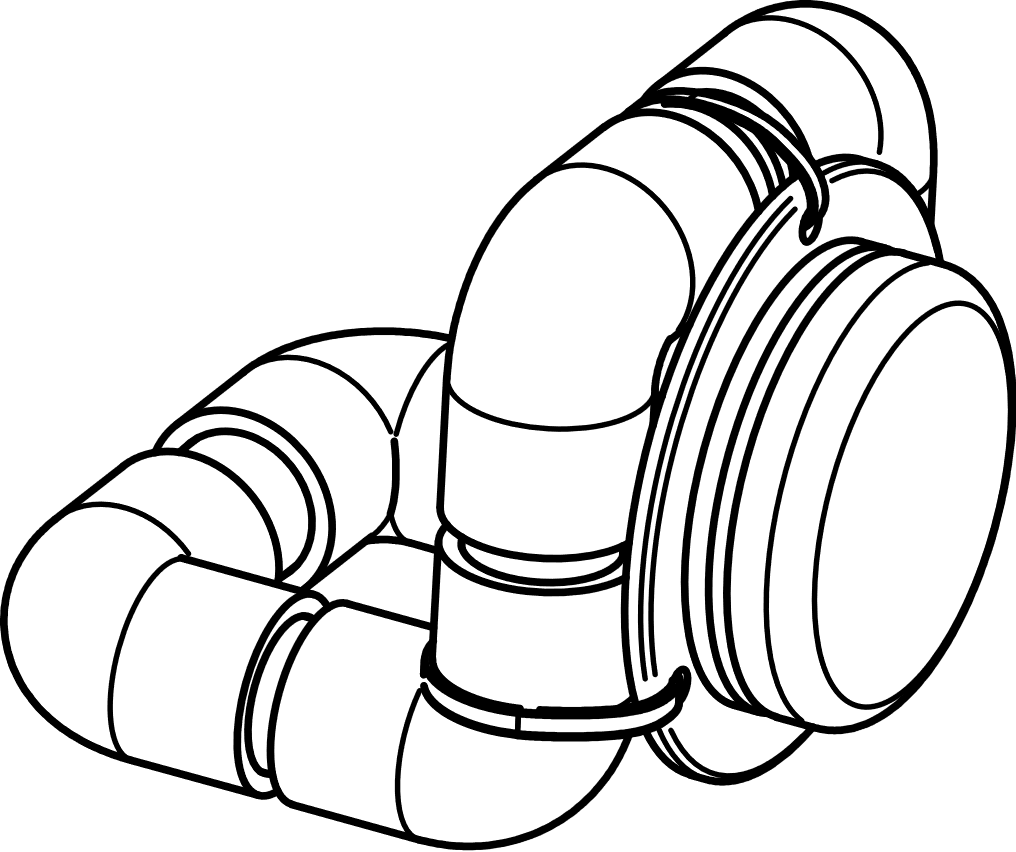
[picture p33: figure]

© 2020 by Neil Squire. “User Guide” licensed under the CC BY SA 4.0 License: http://creativecommons.org/licenses/by-sa/4.0 PAGE 1 OF 3 Design files available at https://www.makersmakingchange.com/project/pams-small-button-mount/

V0.1 | MAY 2020 PAMS: Small Button Mount USER GUIDE

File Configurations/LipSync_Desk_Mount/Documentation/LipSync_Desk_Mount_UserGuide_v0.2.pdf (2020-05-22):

V0.2 | MAY 2020

# PAMS: LipSync Desk Mount

## USER GUIDE

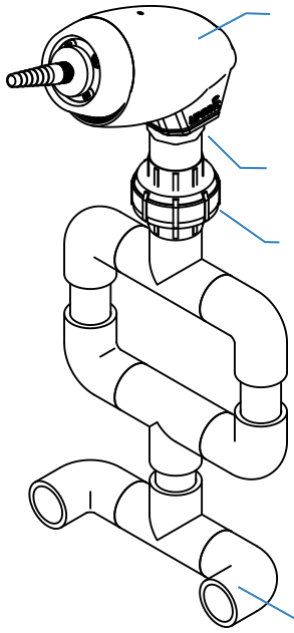
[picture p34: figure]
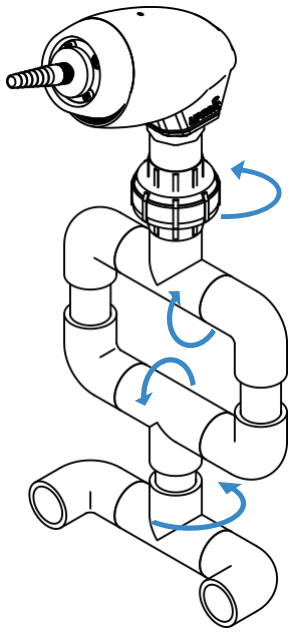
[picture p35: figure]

© 2020 by Neil Squire. (https://neilsquire.ca/) “User Guide” licensed under the CC BY SA 4.0 License: http://creativecommons.org/licenses/by-sa/4.0
Design files available at https://www.makersmakingchange.com/project/pams-small-button-mount/ | PAGE 1 OF 1

### Introduction

The LipSync Desk Mount is a simple mounting solution for mounting the LipSync to a desk or table using a set of PVC piping components and C-clamps.

### Features

### Specifications

Size | W 155 mm x D ~50 mm x H ~300 mm
Cleaning | Wipe with damp cloth
Disinfection | Ethyl Alcohol, Isopropyl Alcohol, Hydrogen Peroxide

### Attaching the LipSync

1. If present, remove the metal threaded adapter and threaded insert by unscrewing them from the bottom of the LipSync.
2. Being careful not to damage the USB cable, thread the PVC Thread Adapter directly into the 3D printed shell of the LipSync. Do not overtighten.

### Mounting to Desk

1. Remove the LipSync from the mount by unscrewing the PVC Union.
2. Use the 2 C-clamps to clamp the bottom PVC Elbows to the table.
3. Reattach the LipSync to the mount by connecting the Union.

### Adjusting the Position

The position of the LipSync can be adjusted by manipulating the PVC joints, which are held by friction.

Thread Adapter

LipSync

Union

Bottom Elbow

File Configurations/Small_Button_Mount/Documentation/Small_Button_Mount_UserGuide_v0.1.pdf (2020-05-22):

V0.1 | MAY 2020

# PAMS: Small Button Mount

## USER GUIDE

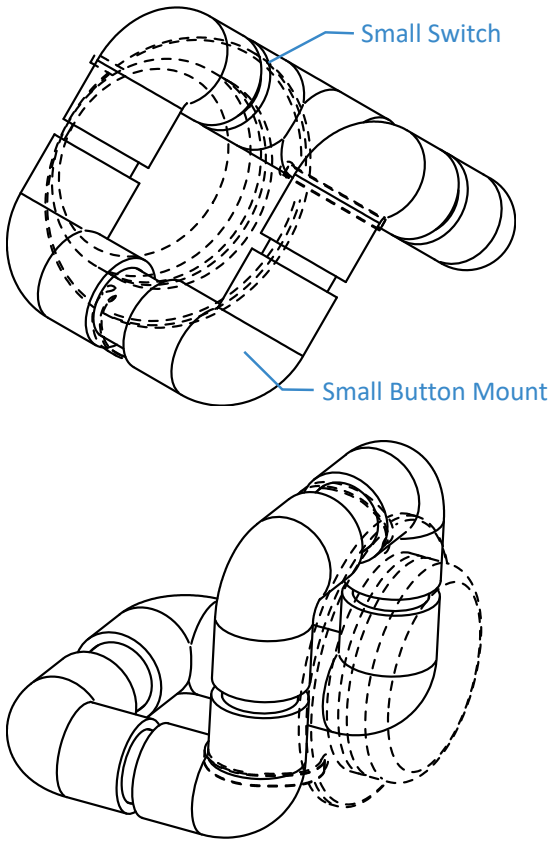
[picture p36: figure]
Small Button Mount; Small Switch
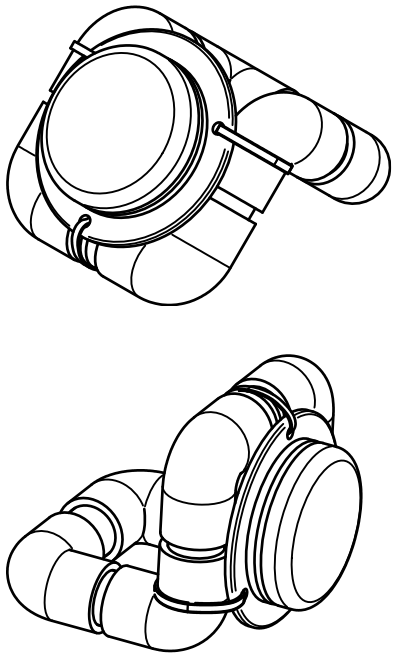
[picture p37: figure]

© 2020 by Neil Squire. (https://neilsquire.ca/) “User Guide” licensed under the CC BY SA 4.0 License: http://creativecommons.org/licenses/by-sa/4.0
Design files available at https://www.makersmakingchange.com/project/pams-small-button-mount/ | PAGE 1 OF 1

### Introduction

The Small Button Mount is a solution for positioning small switches on a flat surface like a desk or table. It can be used to position a switch at an angle or perpendicular to the surface.

### Features

### Specifications

Size | L 96 mm x W 106 mm x H 96 mm
Disinfection | Ethyl Alcohol, Isopropyl Alcohol, Hydrogen Peroxide

### Attaching Switch – Cable Tie

1. Attach button to mount using 3 cable ties (at least 150 mm).
2. Position the mounted switch.

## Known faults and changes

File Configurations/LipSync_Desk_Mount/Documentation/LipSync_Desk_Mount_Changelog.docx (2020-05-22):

V0.2

Changed name from original to fit into PAMS

V0.1

Initial release.

© 2020 by Neil Squire. “Changelog” is licensed under the CC BY SA 4.0 License: http://creativecommons.org/licenses/by-sa/4.0 PAGE 1 OF 3 Design files available at https://www.makersmakingchange.com/project/pams-camera-quick-clamp/

V0.2 | MAY 2020 PAMS: LipSync Desk Mount Changelog

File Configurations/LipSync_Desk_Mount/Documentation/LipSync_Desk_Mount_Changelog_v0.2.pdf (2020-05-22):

V0.2 | MAY 2020

# PAMS: LipSync Desk Mount

# CHANGELOG

© 2020 by Neil Squire. (https://neilsquire.ca/) “Changelog” is licensed under the CC BY SA 4.0 License: http://creativecommons.org/licenses/by-sa/4.0
Design files available at https://www.makersmakingchange.com/project/pams-camera-quick-clamp/ (https://www.makersmakingchange.com/?post_type=project&p=4509&preview=true) | PAGE 1 OF 1

V0.2

# Changed name from original to fit into PAMS

V0.1

Initial release.

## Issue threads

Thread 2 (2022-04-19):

### ISSUE TITLE
README.md has dead link to forum

### ISSUE THREAD

**Issue by Billfred** [makersmakingchange/PVC-Accessible-Mounting-System#2]
The link to the forum thread goes nowhere, presumably due to an old link that didn't get a redirect.

I'm making a baseless guess that it's trying to reach https://makersmakingchange.com/forum/topic/pvc-assistive-mounting-system-2/ but have no firsthand knowledge as someone late to the party.

**Comment by Billfred** [comment]
To be precise, https://github.com/makersmakingchange/PVC-Accessible-Mounting-System/README.md is the page with this issue.  Sorry about that!

**Comment by jakemcivor** [comment]
Thanks. We're slowly updating all of the repositories with updated forum links.

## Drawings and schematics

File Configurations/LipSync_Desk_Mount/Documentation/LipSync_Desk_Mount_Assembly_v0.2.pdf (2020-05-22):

# PAMS: LipSync Desk Mount

# ASSEMBLY GUIDE

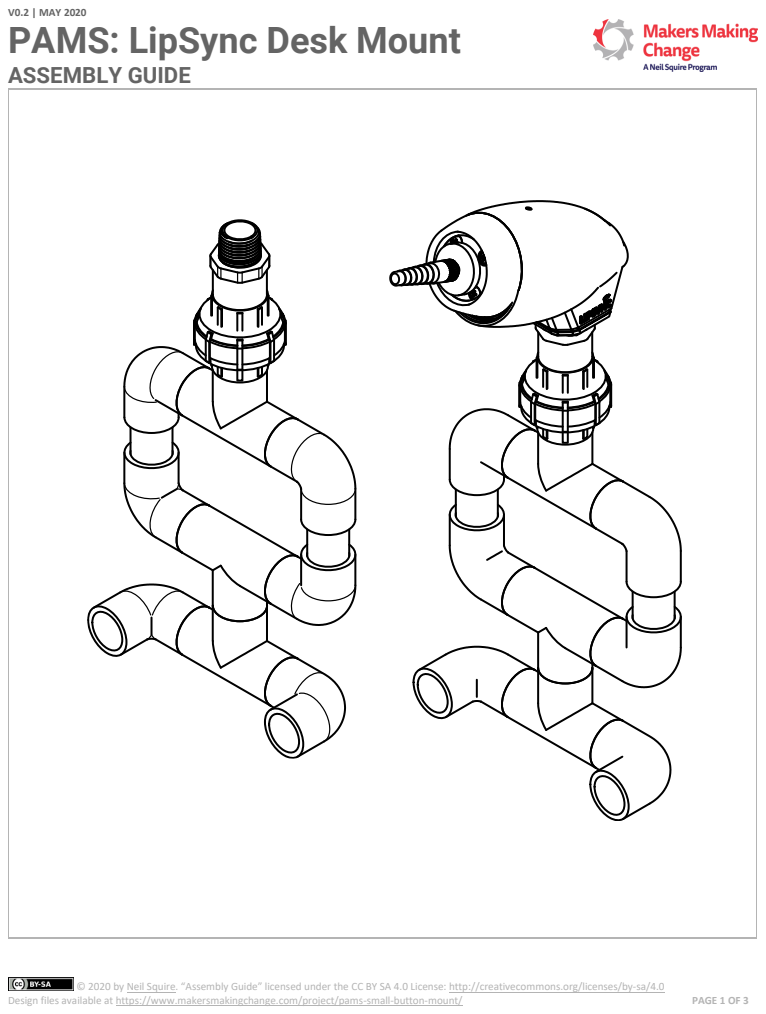
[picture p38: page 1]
V0.2 | MAY 2020; Design files available at https://www.makersmakingchange.com/project/pams-small-button-mount/; PAGE 1 OF 3

© 2020 by Neil Squire. (https://neilsquire.ca/) “Assembly Guide” licensed under the CC BY SA 4.0 License: http://creativecommons.org/licenses/by-sa/4.0

# PAMS: LipSync Desk Mount

# ASSEMBLY GUIDE

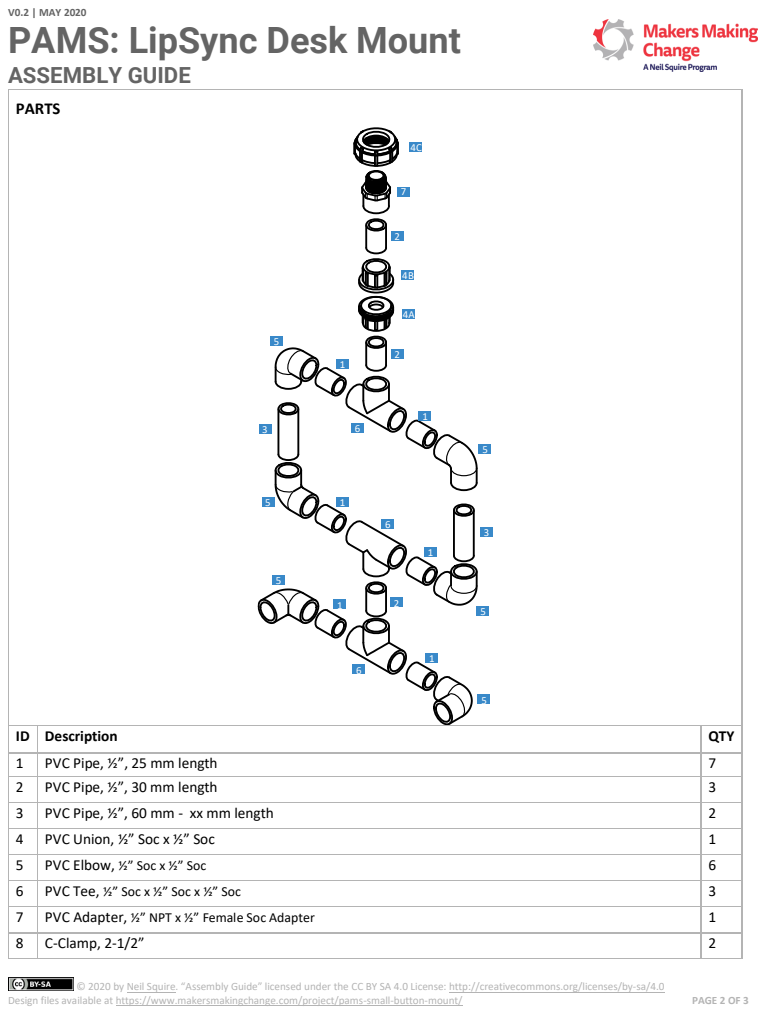
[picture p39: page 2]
Design files available at https://www.makersmakingchange.com/project/pams-small-button-mount/; PAGE 2 OF 3; PARTS

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

# PAMS: LipSync Desk Mount

# ASSEMBLY GUIDE

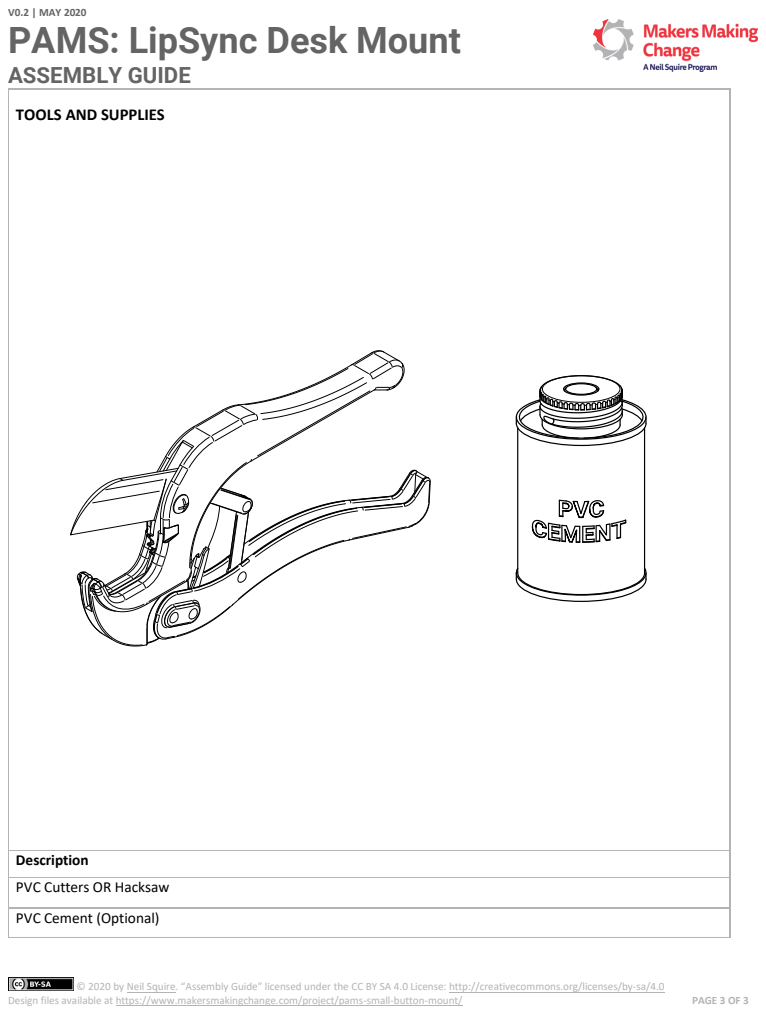
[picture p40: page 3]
Design files available at https://www.makersmakingchange.com/project/pams-small-button-mount/; PAGE 3 OF 3

TOOLS AND SUPPLIES

Description
PVC Cutters OR Hacksaw

PVC Cement (Optional)

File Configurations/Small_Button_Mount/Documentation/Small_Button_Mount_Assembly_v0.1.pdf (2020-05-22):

# PAMS: Small Button Mount

# ASSEMBLY GUIDE

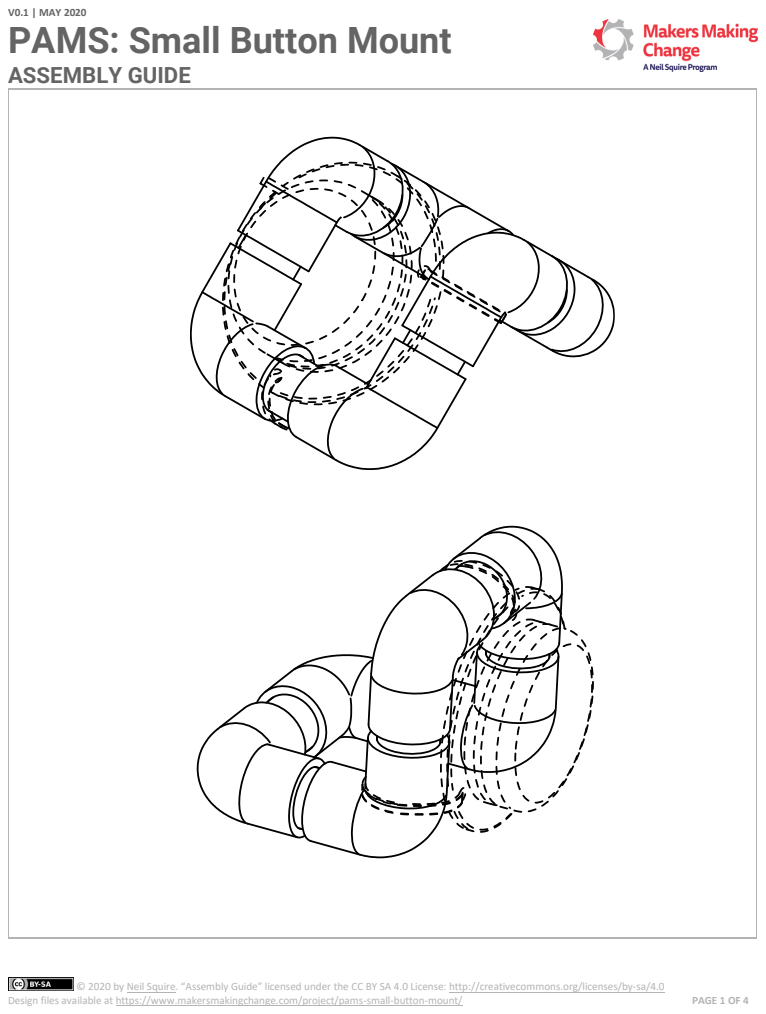
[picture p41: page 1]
V0.1 | MAY 2020; Design files available at https://www.makersmakingchange.com/project/pams-small-button-mount/; PAGE 1 OF 4

© 2020 by Neil Squire. (https://neilsquire.ca/) “Assembly Guide” licensed under the CC BY SA 4.0 License: http://creativecommons.org/licenses/by-sa/4.0

# PAMS: Small Button Mount

# ASSEMBLY GUIDE

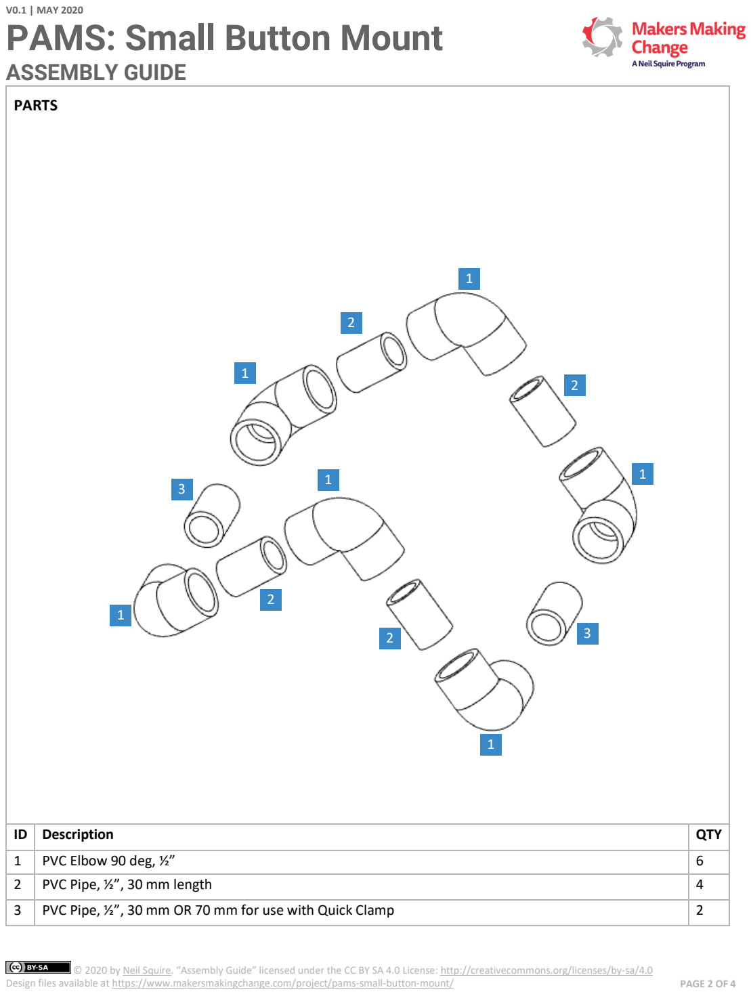
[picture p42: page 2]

Design files available at https://www.makersmakingchange.com/project/pams-small-button-mount/ | PAGE 2 OF 4

## PARTS

ID | Description | QTY
1 | PVC Elbow 90 deg, ½” | 6
2 | PVC Pipe, ½”, 30 mm length | 4
3 | PVC Pipe, ½”, 30 mm OR 70 mm for use with Quick Clamp | 2

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
# PAMS: Small Button Mount

# ASSEMBLY GUIDE

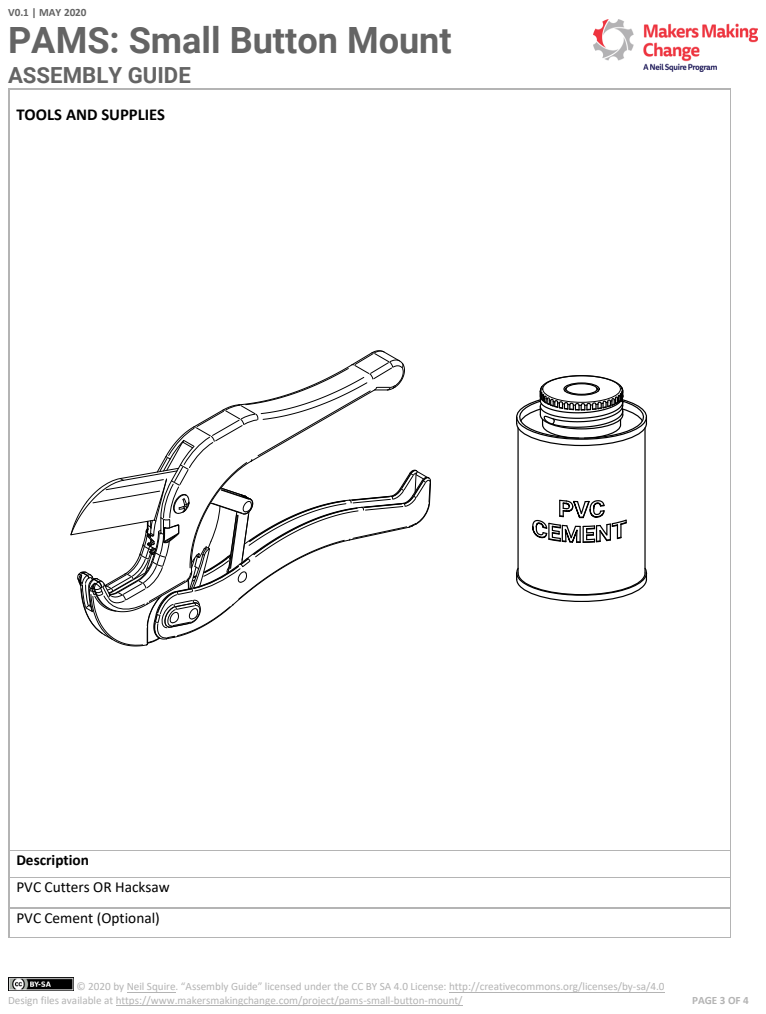
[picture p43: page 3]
Design files available at https://www.makersmakingchange.com/project/pams-small-button-mount/; PAGE 3 OF 4

TOOLS AND SUPPLIES

Description
PVC Cutters OR Hacksaw

PVC Cement (Optional)

# PAMS: Small Button Mount

# ASSEMBLY GUIDE

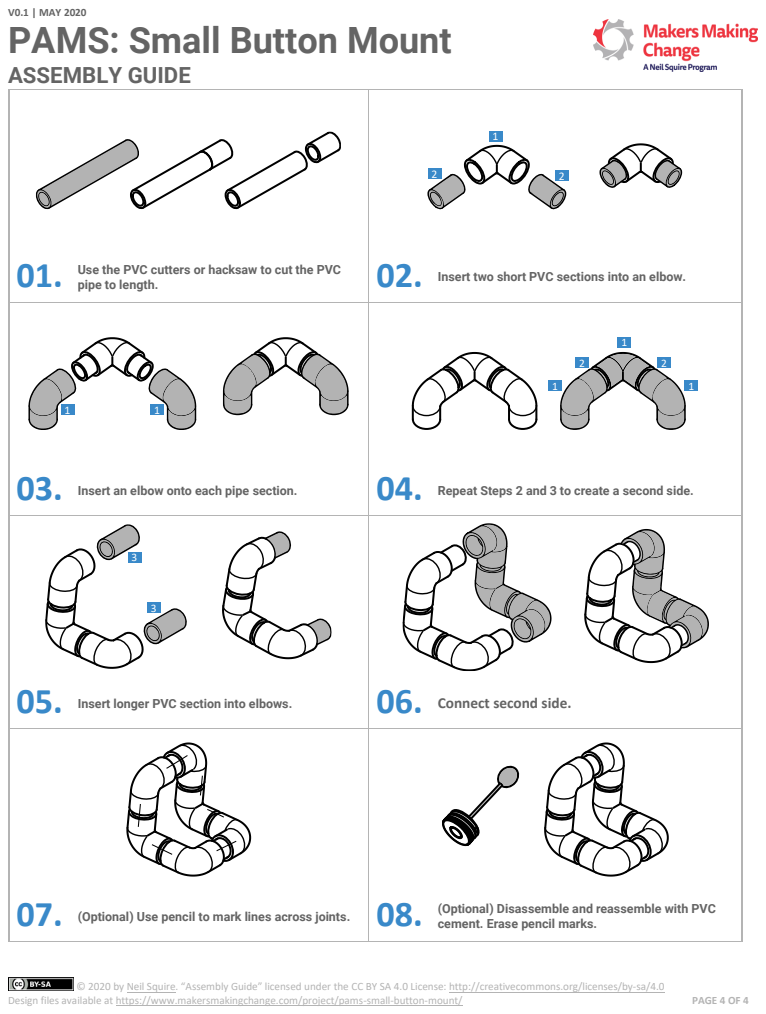
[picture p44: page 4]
Design files available at https://www.makersmakingchange.com/project/pams-small-button-mount/; PAGE 4 OF 4

01. Use the PVC cutters or hacksaw to cut the PVC pipe to length. | 02. Insert two short PVC sections into an elbow.

03. Insert an elbow onto each pipe section. | | 04. Repeat Steps 2 and 3 to create a second side.

3 3 05. Insert longer PVC section into elbows. | | 06. Connect second side.

07. (Optional) Use pencil to mark lines across joints. | | 08. (Optional) Disassemble and reassemble with PVC cement. Erase pencil marks.

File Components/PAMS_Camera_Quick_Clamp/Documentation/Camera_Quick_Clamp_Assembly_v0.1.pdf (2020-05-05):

# PAMS: Camera Quick Clamp

# ASSEMBLY GUIDE

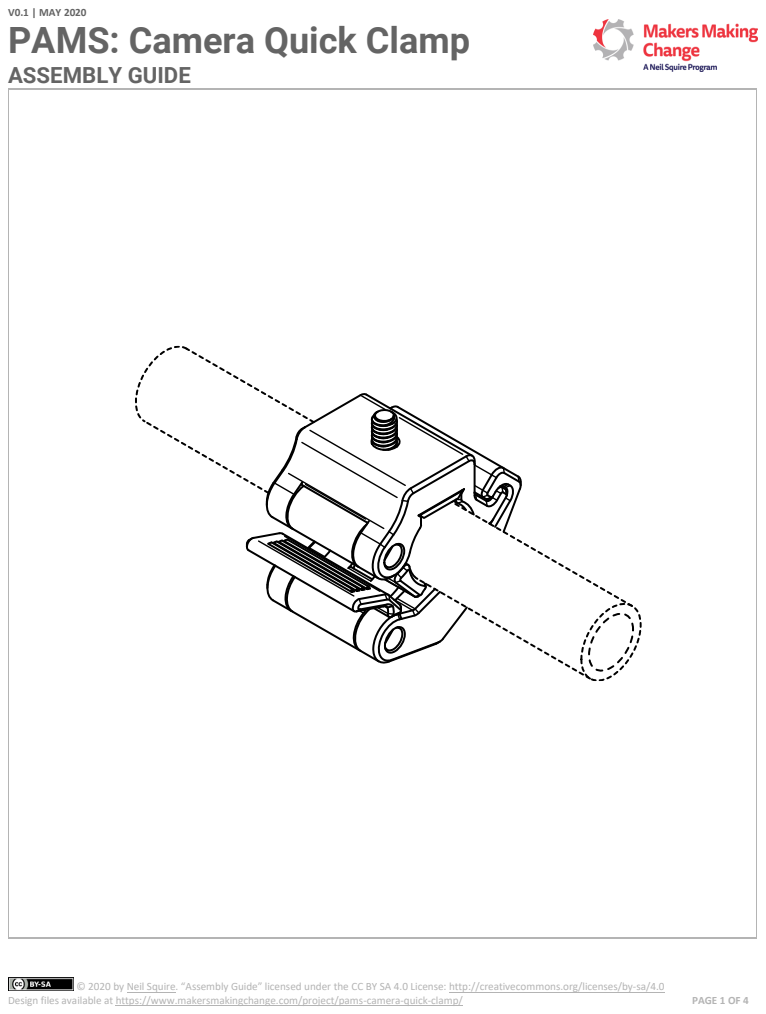
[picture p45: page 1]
V0.1 | MAY 2020; Design files available at https://www.makersmakingchange.com/project/pams-camera-quick-clamp/; PAGE 1 OF 4

© 2020 by Neil Squire. (https://neilsquire.ca/) “Assembly Guide” licensed under the CC BY SA 4.0 License: http://creativecommons.org/licenses/by-sa/4.0

# PAMS: Camera Quick Clamp

# ASSEMBLY GUIDE

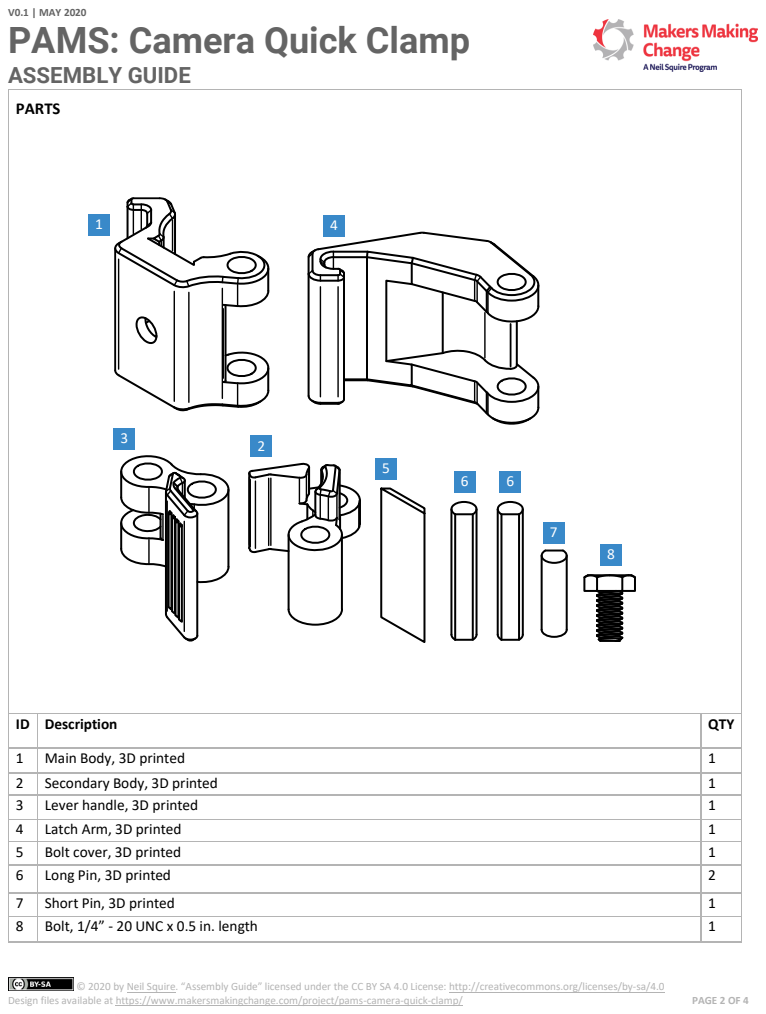
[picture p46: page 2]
Design files available at https://www.makersmakingchange.com/project/pams-camera-quick-clamp/; PAGE 2 OF 4; PARTS

ID | Description | QTY

1 | Main Body, 3D printed | 1
2 | Secondary Body, 3D printed | 1
3 | Lever handle, 3D printed | 1
4 | Latch Arm, 3D printed | 1
5 | Bolt cover, 3D printed | 1
6 | Long Pin, 3D printed | 2
7 | Short Pin, 3D printed | 1
8 | Bolt, 1/4” - 20 UNC x 0.5 in. length | 1

# PAMS: Camera Quick Clamp

# ASSEMBLY GUIDE

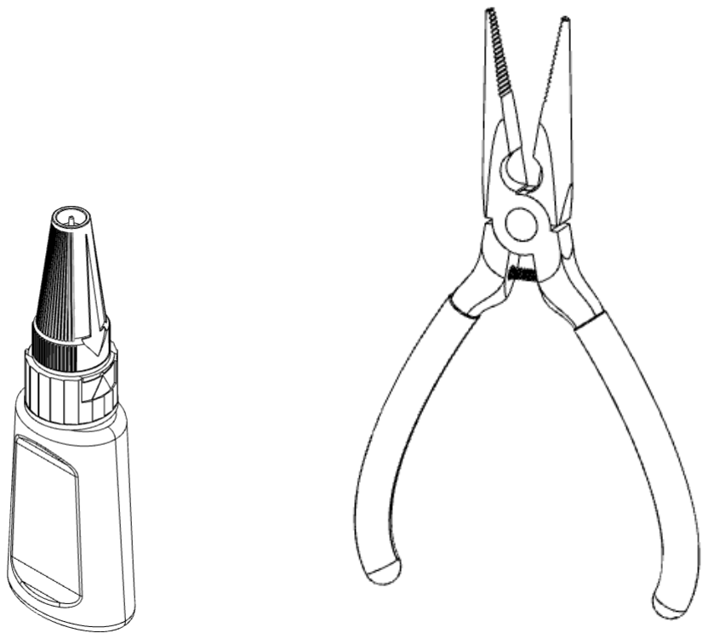
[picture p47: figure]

Design files available at https://www.makersmakingchange.com/project/pams-camera-quick-clamp/ (https://www.makersmakingchange.com/?post_type=project&p=4509&preview=true) | PAGE 3 OF 4

## TOOLS AND SUPPLIES

## Description

## Superglue

## Needle nose pliers (Optional)

# PAMS: Camera Quick Clamp

# ASSEMBLY GUIDE

Design files available at https://www.makersmakingchange.com/project/pams-camera-quick-clamp/ (https://www.makersmakingchange.com/?post_type=project&p=4509&preview=true) | PAGE 4 OF 4
1 01. Remove built-in support material from main body. | 2 02. Remove built-in support material from secondary body.
3 03. Remove built-in support material from lever handle. | 4 04. Remove built-in support material from latch arm.
7 6 6 1 2 3 4 05. Assemble main body, secondary body, lever handle and latch arm as shown with long and short pins. | 8 06. Insert bolt into main body.
5 07. Slide bolt cover into slot in main body. | 08. Use a drop of superglue on each of the pins and the bolt cover slot.

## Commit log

2020-05-05 Initial commit of Camera Quick Clamp
    [CQC.stl, CQC_BoltCover.stl, CQC_LatchArm.stl, CQC_LeverHandle.stl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]
2020-05-14 Update README.md
    Correct CAD and 3D printing links
2020-05-19 Initial commit Small Button Mount
    [Small_Button_Mount_BOM.xlsx]
2020-05-20 Update README.md
    Add small button mount links
2020-05-20 Update User Guide
    Add cable tie info.
2020-05-22 Update LipSync Desk Mount to v0.2
    [LipSync_Desk_Mount_BOM.xlsx]
2020-06-17 Update CQC 3D printing info
    Add print orientation photo and document with print settings.
2020-06-17 Update CQC 3D Printing Readme
    Add note about built-in support
